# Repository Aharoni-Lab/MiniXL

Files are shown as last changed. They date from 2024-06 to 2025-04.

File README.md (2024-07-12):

# Miniscope extra Large FOV (MiniXL) 

**[[Miniscope V4 Wiki](https://github.com/Aharoni-Lab/Miniscope-v4/wiki)] [[Miniscope DAQ Software Wiki](https://github.com/Aharoni-Lab/Miniscope-DAQ-QT-Software/wiki)] [[Miniscope DAQ Firmware Wiki](https://github.com/Aharoni-Lab/Miniscope-DAQ-Cypress-firmware/wiki)] [[Miniscope Wire-Free DAQ Wiki](https://github.com/Aharoni-Lab/Miniscope-Wire-Free-DAQ/wiki)] [[MiniLFOV-Light Wiki](https://github.com/Aharoni-Lab/Miniscope-LFOV/wiki)][[2021 Virtual Miniscope Workshop Recording](https://sites.google.com/metacell.us/miniscope-workshop-2021)]**

This is the repository for the second version of MiniLFOV, called MiniXL, which is able to image the neuronal acitivity in freely moving mice with a field of view larger than 3mm and single cell resolution.
Large field-of-view miniature microscope for freely moving mice and bigger animals. 
<p align="center">
  
</p>
<p dir="auto"><strong>All information, guides, and tutorials can be found on the <a href="https://github.com/Aharoni-Lab/MiniLFOV-Light?tab=readme-ov-file">MiniLFOV-Light Wiki Page</a>.</strong></p>
<p dir="auto"><strong>Make sure to click Watch and Star in the upper right corner of this page to get updates on new features and releases.</strong></p>
<p align="center" dir="auto">
<p dir="auto">The MiniXL is designed to extend the capabilities of the UCLA Miniscope for imaging in freely moving mice, and imaging to larger rodents and non-human primates. This system is capable of multiple imaging configurations, including deep brain imaging using implanted optical probes and cortical imaging through cranial windows. Some feature highlights are listed below.</p>
<ul dir="auto">
<li>3.5 mm field of view</li>
<li>~3 µm resolution</li>
<li>1.9 mm working distance</li>
<li>+/-200 µm electronic focal adjustment</li>
<li>Modular optics</li>
<li>Achromatic optics</li>
<li>3.5 grams</li>
<li>30 mm tall</li>
<li>Absolute head orientation sensor</li>
<li>Requires ~1/2th the excitation power of previous systems</li>
<li>No more soldering!</li>
<li>Still uses only a single coaxial cable (down to 0.3mm in diameter) for power, communication, and data.</li>
<li>New DAQ software</li>
</ul>
<p align="center">
  
</p>

## How to use with the Miniscope DAQ Software
The MiniXL needs an updated videoDevices.json file which holds the configuration data for different modes the MiniLFOV-XL is able to run in. This file can be found in the Miniscope_DAQ_Software_Configurations folder in this repository and should replace the same named fiel in the deviceConfig folder of the Miniscope Software.

We have also included an example user configuration file that will run the MiniLFOV-XL in its 2x binning and summing mode.

## How to cite
A paper discussing the MiniLFOV and Miniscope Wire-Free DAQ can be found [here](https://www.science.org/doi/10.1126/sciadv.adg3918). Please use the following citation information.

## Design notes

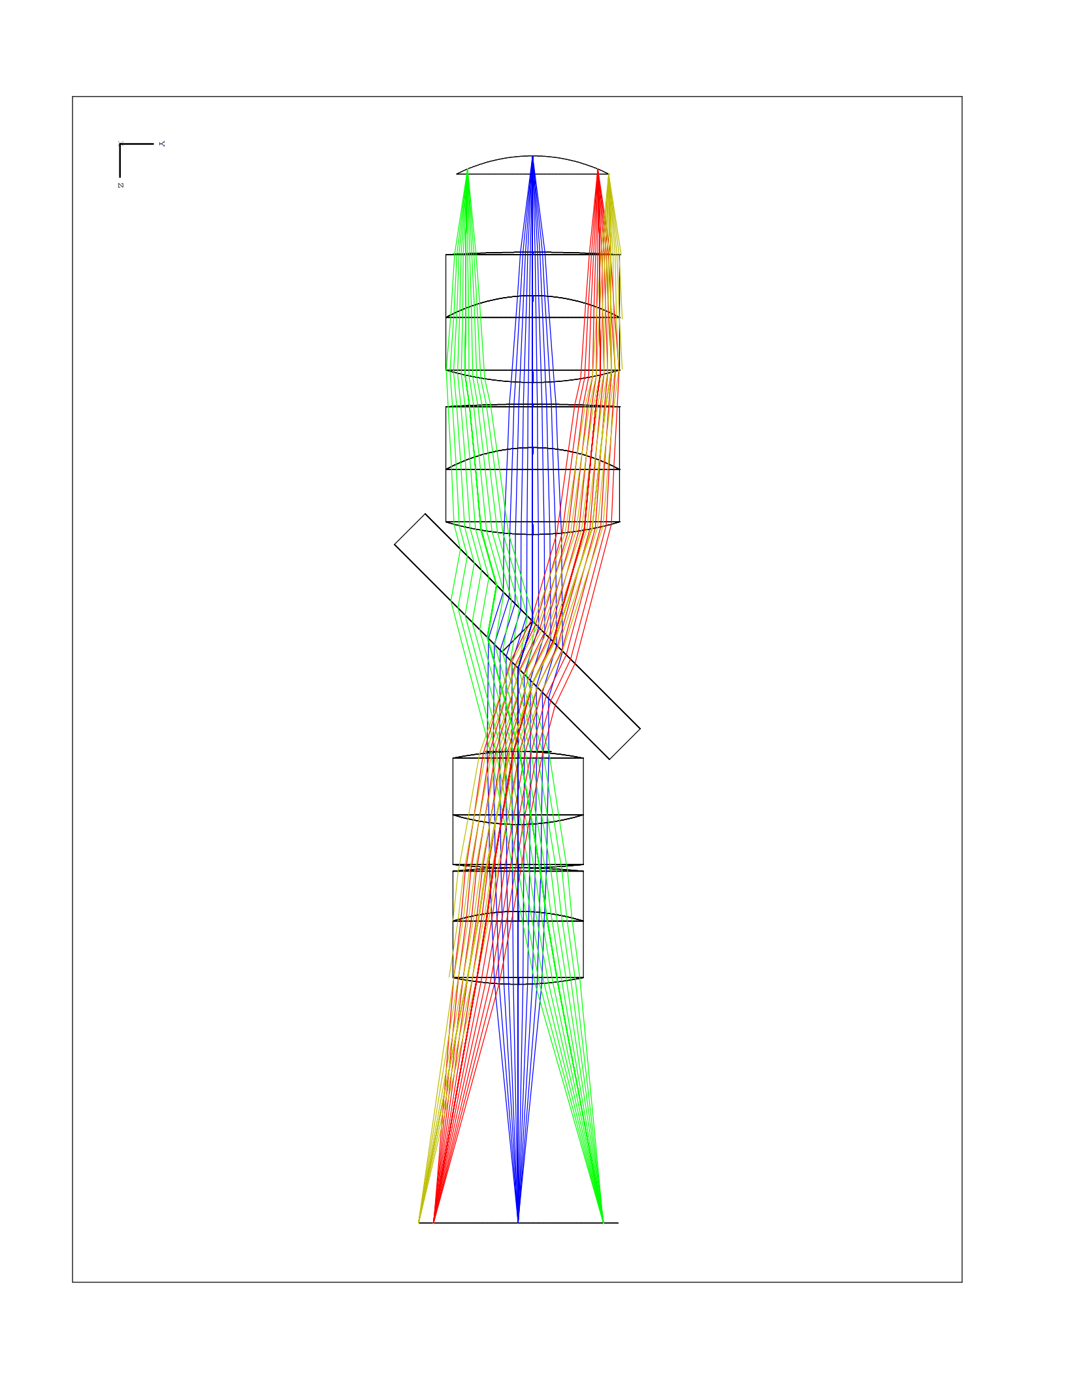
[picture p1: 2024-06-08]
Zemax/Mini_V4_FOV-3mm_NA-0d2_Good_Final1_07072020_00.png

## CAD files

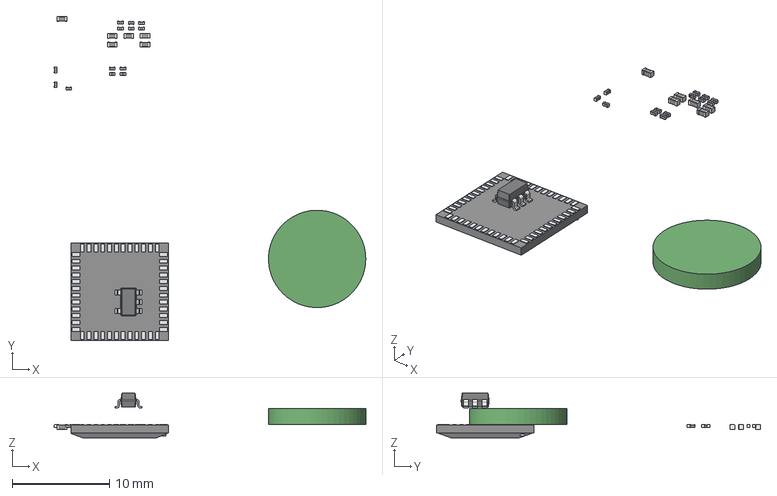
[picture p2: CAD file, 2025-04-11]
KiCad/Kicad_LFOV_RigidFlex_Assembly.step
32.0 x 33.3 x 4.60 mm

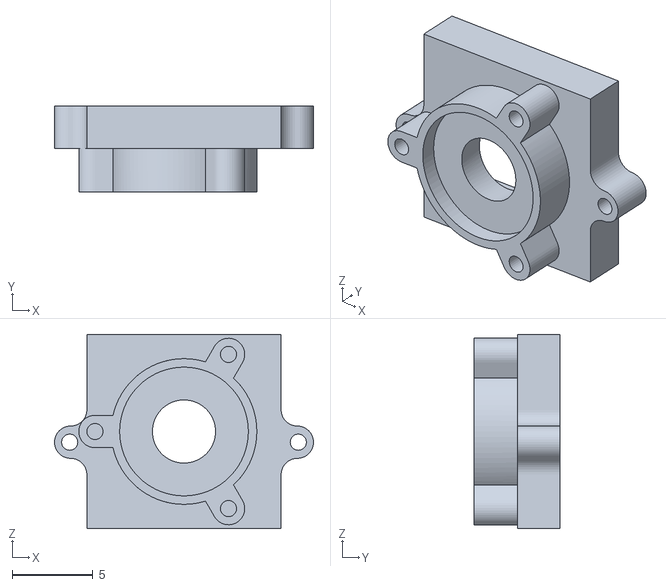
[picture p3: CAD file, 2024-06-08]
3d-Printed-Bodies/CScope_Body_Part2_07092020.stl
16.0 x 5.28 x 12.0

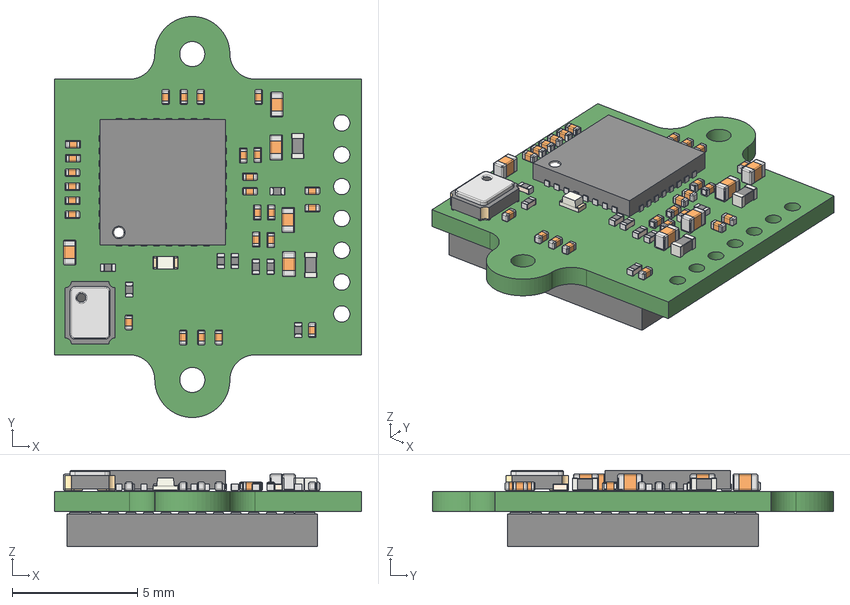
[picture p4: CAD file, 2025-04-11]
KiCad/cMOS_PCB.step
12.2 x 16.0 x 3.04 mm

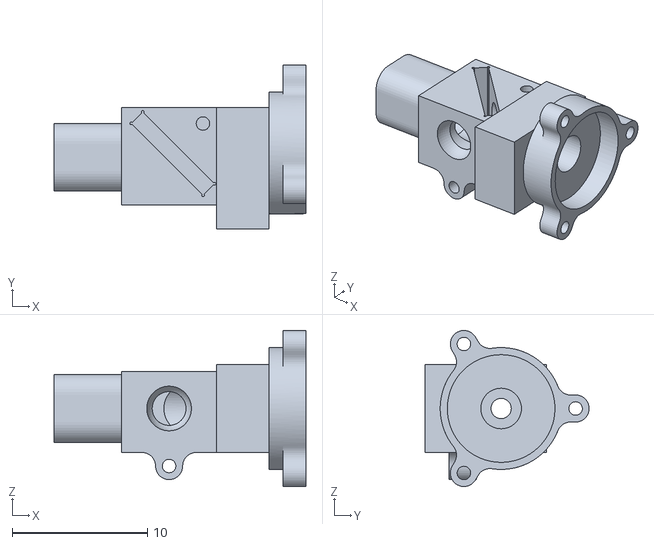
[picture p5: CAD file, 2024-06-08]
3d-Printed-Bodies/CScope_Body_Part1_07092020.stl
18.6 x 12.1 x 11.5

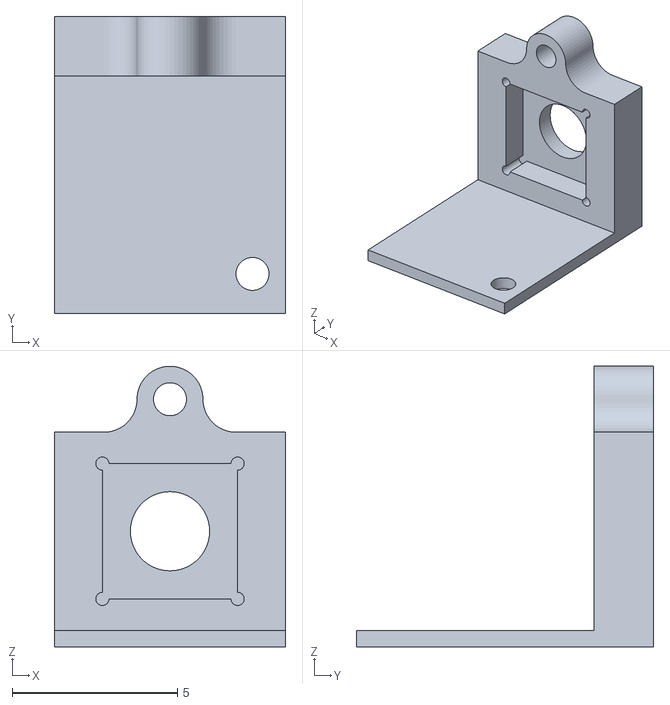
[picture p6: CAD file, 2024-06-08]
3d-Printed-Bodies/CScope_Body_Part3_07092020.stl
7.00 x 9.00 x 8.50

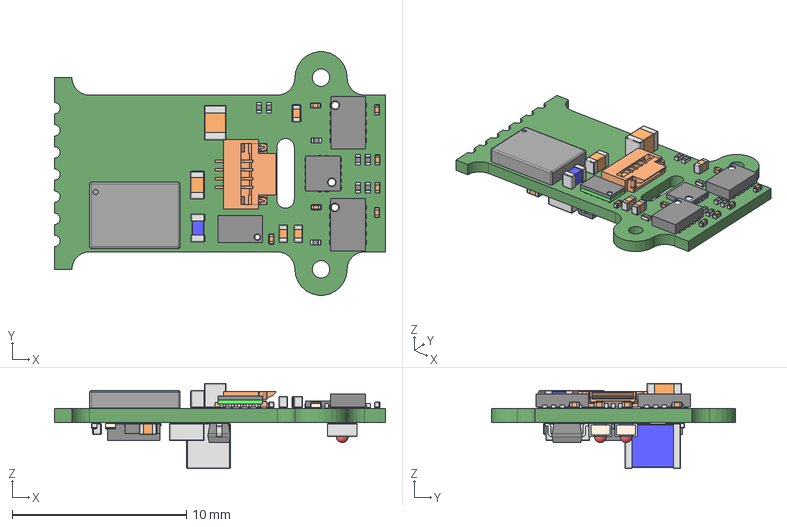
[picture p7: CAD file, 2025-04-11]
KiCad/led_PCB.step
19.0 x 14.0 x 4.89 mm

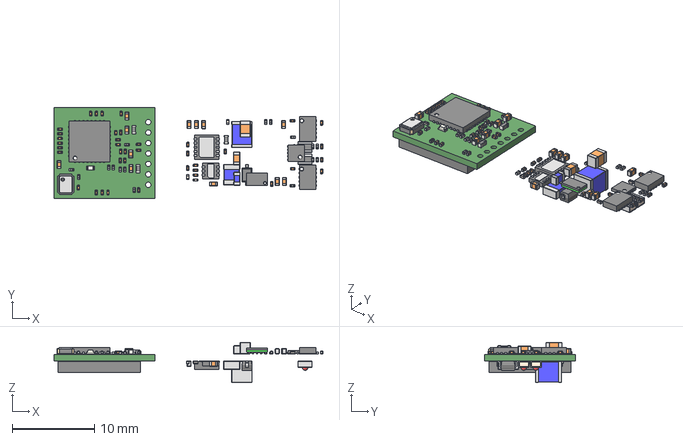
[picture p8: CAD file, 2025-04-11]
KiCad/Kicad_LFOV_RigidFlex_Assembly_Screwhole.step
32.7 x 11.0 x 4.89 mm

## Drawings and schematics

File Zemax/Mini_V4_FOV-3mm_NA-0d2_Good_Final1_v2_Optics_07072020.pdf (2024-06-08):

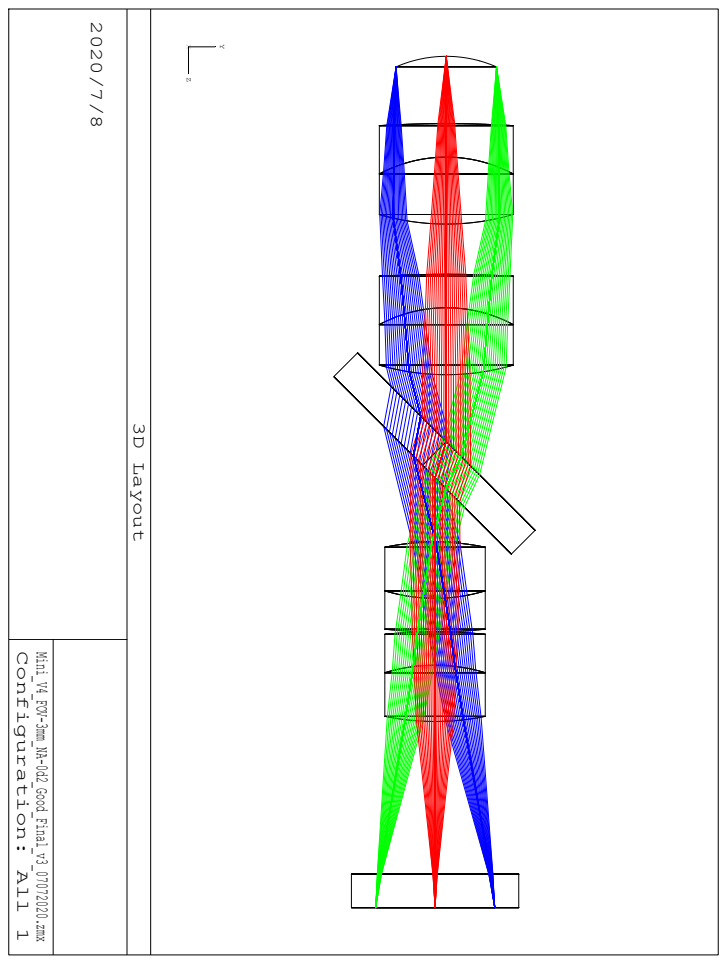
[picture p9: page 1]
Configuration: All 1 Mini_V4_FOV-3mm_NA-0d2_Good_Final_v3_07072020.zmx; 3D Layout

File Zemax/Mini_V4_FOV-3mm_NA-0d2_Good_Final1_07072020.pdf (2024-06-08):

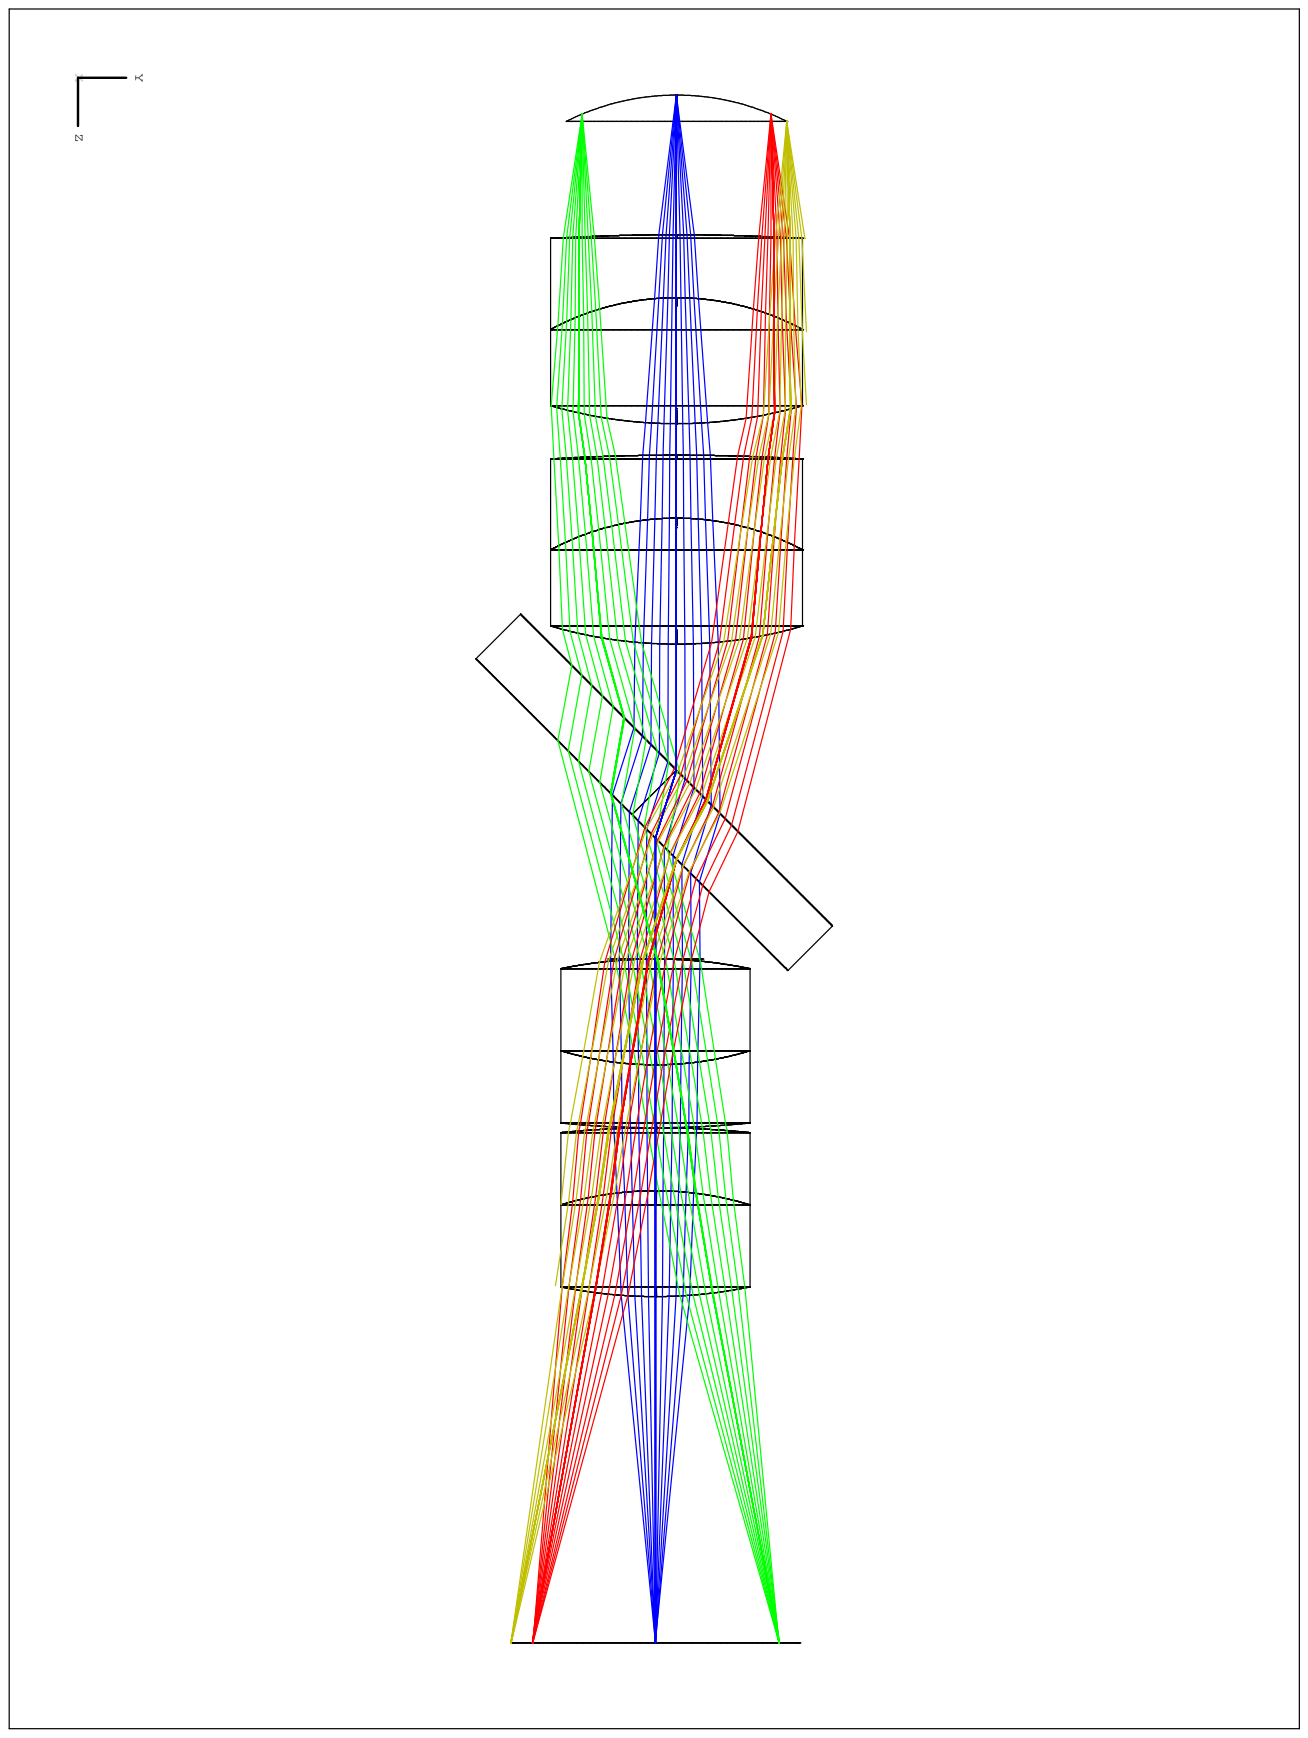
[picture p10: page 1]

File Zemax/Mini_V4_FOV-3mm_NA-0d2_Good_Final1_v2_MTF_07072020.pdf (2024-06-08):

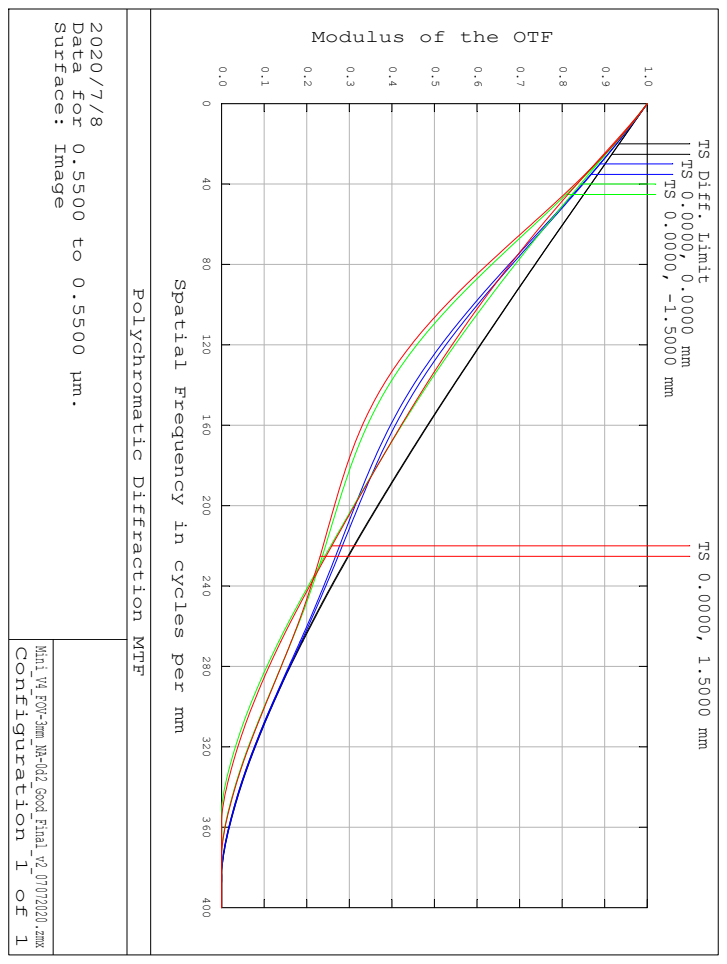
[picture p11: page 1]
Configuration 1 of 1; Mini_V4_FOV-3mm_NA-0d2_Good_Final_v2_07072020.zmx; Surface: Image

Data for 0.5500 to 0.5500 µm.

Modulus of the OTF

TS Diff. Limit

Spatial Frequency in cycles per mm

Polychromatic Diffraction MTF

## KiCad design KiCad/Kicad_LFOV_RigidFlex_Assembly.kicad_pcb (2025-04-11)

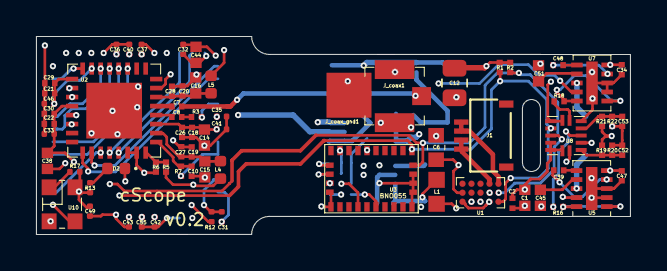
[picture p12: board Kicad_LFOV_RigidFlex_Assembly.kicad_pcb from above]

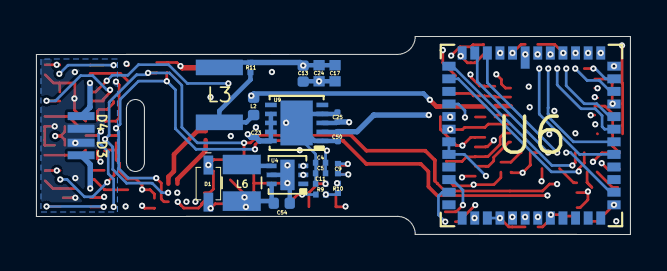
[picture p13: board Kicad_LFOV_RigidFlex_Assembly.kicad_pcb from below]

Board: 4 copper layers, 33.0 x 11.0 mm, 95 parts (23 on the bottom side), 56 nets.

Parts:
C1, C14, C15, C45, C51: GRM155R60J475ME87D; C_0402_1005Metric_L
C2, C5, C7, C9, C11, C18, C19, C20, C21, C22, C52, C53: GRM033R61A104ME15D; C_0201_0603Metric_L
C4, C26, C27, C28, C29, C30: GRM033R71A103KA01D; C_0201_0603Metric_L
C6: GRJ188R72A104KE11D; C_0603_1608Metric_L
C8: GRM033R61C473KE84D; C_0201_0603Metric_L
C10: GRM033R61A105ME15D; R_0201_0603Metric_ERJ_L
C12: GRM21BR61A476ME15L; C_0805_2012Metric_L
C13, C38: 10uF; C_0402_1005Metric_L
C16, C17, C24, C44: GRM155R60J106ME15D; C_0402_1005Metric_L
C23, C25, C31, C32, C33, C50: 1uF; C_0201_0603Metric_L
C34, C39, C47, C48: GRM033R61A225ME47D; C_0201_0603Metric_L
C35, C36, C37, C40, C41, C42, C43, C46, C55: 0.1uF; C_0201_0603Metric_L
C49: 10nF; C_0201_0603Metric_L
C54: 22uF; C_0402_1005Metric_L
D1: BAS316-TP; SOD_323_250X125X110L30X32L
D2: LED 0402; LED_0402_1005Metric
D3, D4: LXZ1-PB01; LED_LXZ1_PR01_L
J1: FH19C-4S-0.5SH(10)
J_coax1: U.FL-R-SMT-1(10); Coax_Conn_U.FL
J_coax_gnd1: Conn_01x01; Conn_1x1_100x100_Pad
L1: LQM18PN3R3MGHD; L_0603_1608Metric_L
L2, L4, L5: BLM15HD102SN1D; L_0402_1005Metric
L3: ADL3225V-470MT-TL000; L_1210_3225Metric_L
L6: LQM2HPN1R0MG0; L_1008_2520Metric_L
R1, R2: ERJ-1GNF3321C; R_0201_0603Metric_ERJ_L
R3: ERJ-1GNF49R9C; R_0201_0603Metric_ERJ_L
R5, R7, R9, R10, R16: ERJ-1GNF1022C; R_0201_0603Metric_ERJ_L
R6: ERJ-1GNF1003C; R_0201_0603Metric_ERJ_L
R11: ERJ-1GNF1801C; R_0201_0603Metric_ERJ_L
R12: 1k; R_0201_0603Metric_ERJ_L
R13: 500; R_0201_0603Metric_ERJ_L
R17: DNL; R_0201_0603Metric_ERJ_L
R18: ERJ-1GEF1022C; R_0201_0603Metric_ERJ_L
R19, R21: ERJ-1GNJ622C; R_0201_0603Metric_ERJ_L
R20, R22: ERJ-1GNF3741C; R_0201_0603Metric_ERJ_L
U1: MAX14574EWL+; BGA_15_NP50_3X5_155X255X69B31N
U2: DS90UB913ATRTVTQ1; QFN_33_P50_500X500X80L40X24T310L
U3: BNO055; LGA28R50P4X10_380X520X100
U4: SC189ZULTRT; SON_7P50_200X200X57L35X24T170X80N
U5, U7: LTC3218; SON_11_P50_300X200X80L40X25T239X64L
U6: MT9P031I12STM-DP; iLCC48P70_1000X1000X135L80X40N
U8: TPL0102-100RUCR; QFN_14_P40_200X200X40L40X20L
U9: NCV8154MW180280TBG; DFN10_3x3_11P50_300X300X100L40X24T250X180N
U10: SG-210STF 66.6667ML3; OSC_CC250X200X80L70X75L

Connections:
+3V3: C1.1, C2.1, C4.1, C5.1, C9.2, C12.1, C23.1, C34.1, C47.1, C54.1, L1.1, L6.2, R1.2, R2.2, R9.1, R10.1, R19.1, R21.1, U1.A3, U1.B2, U3.3, U3.28, U4.6, U5.10, U7.10, U8.14, U9.7, U9.8, U9.9, U9.10
+5V: C13.1, C17.1, C24.1, L3.2, R11.1, U4.2, U4.3
/CAP: C11.2, U3.9
/ENT: U2.15, U5.4, U7.4
/EWL1: J1.1, J1.2, U1.C2
/EWL2: J1.3, J1.4, U1.C1
/EXTCLK: U6.31, U10.3
/RESET_BAR: C31.1, R12.2, U6.16
/Va: C52.1, R19.2, R20.1, U8.1
/Vb: C53.1, R21.2, R22.1, U8.4
/_Wa: R16.1, U8.3
/_Wb: R18.1, U8.6
CLK_OUT: U2.3, U6.32
DIN0: U2.19, U6.35
DIN1: U2.20, U6.36
DIN2: U2.21, U6.37
DIN3: U2.22, U6.38
DIN4: U2.23, U6.40
DIN5: U2.24, U6.41
DIN6: U2.26, U6.42
DIN7: U2.27, U6.43
DIN8: U2.29, U6.44
DIN9: U2.30, U6.45
DOUT_P: C7.1, J_coax1.2, L2.1
FV: U2.2, U6.7
GND: C1.2, C2.2, C4.2, C5.2, C6.2, C9.1, C10.2, C11.1, C12.2, C13.2, C14.2, C15.2, C16.2, C17.2, C18.2, C19.2, C20.2, C21.2, C22.2, C23.2, C24.2, C25.2, C26.2, C27.2, C28.2, C29.2, C30.2, C31.2, C32.2, C33.2, C34.2, C35.2, C36.2, C37.2, C38.2, C40.2, C41.2, C42.2, C43.2, C44.2, C45.2, C46.2, C47.2, C49.2, C50.2, C51.2, C52.2, C53.2, C54.2, C55.2, D2.1, D3.C, D4.C, J_coax1.1, J_coax_gnd1.1, R3.1, R6.2, R20.2, R22.2, U1.A2, U1.A5, U2.6, U2.7, U2.33, U3.2, U3.5, U3.6, U3.15, U3.16, U3.17, U3.18, U3.25, U4.5, U4.7, U5.7, U5.8, U5.11, U6.2, U6.3, U6.6, U6.10, U6.17, U6.20, U6.21, U6.22, U6.26, U6.46, U7.7, U7.8, U7.11, U8.2, U8.5, U8.7, U8.8, U8.11, U8.12, U8.13, U9.1, U9.4, U9.11, U10.2
I2C_SCL: R2.1, U1.B1, U2.4, U3.19, U6.4, U8.10
I2C_SDA: R1.1, U1.A1, U2.5, U3.20, U6.5, U8.9
LV: U2.1, U6.8
MODE: R5.2, R6.1, U2.8
unnamed: C6.1, D1.C, U1.B5
unnamed: C7.2, U2.13
unnamed: C8.1, R3.2
unnamed: C8.2, U2.12
unnamed: C39.1, U5.9
unnamed: C39.2, U5.1
unnamed: C45.1, U5.2
unnamed: C48.1, U7.9
unnamed: C48.2, U7.1
unnamed: C51.1, U7.2
unnamed: D1.A, L1.2, U1.A4
unnamed: D2.2, R13.1
unnamed: D3.A, U5.3
unnamed: D4.A, U7.3
unnamed: L2.2, L3.1, R11.2
unnamed: L6.1, U4.4
unnamed: R9.2, U3.11
unnamed: R10.2, U3.4
unnamed: R16.2, U5.5, U5.6
unnamed: R17.2, U10.1
unnamed: R18.2, U7.5, U7.6
PDB: C10.1, R7.2, U2.9
VDDCML: C16.1, C20.1, C28.1, L5.1, U2.14
VDDD: C14.1, C18.1, C22.1, C26.1, C30.1, C33.1, C36.1, C38.1, C41.1, C50.1, L4.2, L5.2, R5.1, U2.11, U2.28, U6.12, U6.47, U9.2
VDDIO: C21.1, C25.1, C29.1, C32.1, C35.1, C37.1, C40.1, C42.1, C43.1, C44.1, C46.1, C49.1, C55.1, R7.1, R12.1, R13.2, R17.1, U2.25, U6.1, U6.11, U6.13, U6.14, U6.23, U6.24, U6.25, U6.39, U6.48, U9.3, U10.4
VDDPLL: C15.1, C19.1, C27.1, L4.1, U2.10
